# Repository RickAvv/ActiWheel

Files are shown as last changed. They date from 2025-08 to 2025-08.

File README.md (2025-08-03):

# ActiWheel
Complex activity wheel for mice behavioural research

The wheel is very simple in its implementation, as it has an arduino MEGA 2560 with a [logger shield](https://www.az-delivery.uk/products/datenlogger-modul) at its core.  The wheel axel is the shaft of a continuous potentiometer so that the exact position of the wheel in the radial axis can be logged, at a frequency of 100 Hz. 

The potentiometer it was designed to work with can be found [here](https://uk.rs-online.com/web/p/potentiometers/6930746), although any continuous potentiometer would do. A possible improvement on the design would come from the implementation of a rotary encoder instead of a potentiometer.  
  
## Assembly instructions:  
1) Print all the parts - the rungs have a bigger circular base for printing stability that should be snapped away with wire cutters or other tool.   
  
2) Assemble the Base and the Box with M3 countersunk screws of appropriate length.  

3) Attach the Arduino onto the Lid with M3 countersunk screws and M3 nuts. Mount the logger shield. Insert the SD card.  
  
4) Use dupont wires or soldering to connect the potentiometer to 5V, ground and A8 (middle potentiometer pin). Mount the potentiometer onto the Box with its hex nut. Slot the Connector onto the potentiometer shaft, and mount the Wheel onto the Connector with an M3 screw (center of Wheel).  
  
5) To power the arduino, externalise 2 wires from 5V and ground through the small slit on top of the Box, ideally soldered to a female 5V jack to be connected to a wall 9V power supply. Make sure to use plastic or metal shielding for the part that is still inside the mouse cage to avoid them being chewed.  
  
6) Mount the Lid onto the Box with countersank M3 screws.

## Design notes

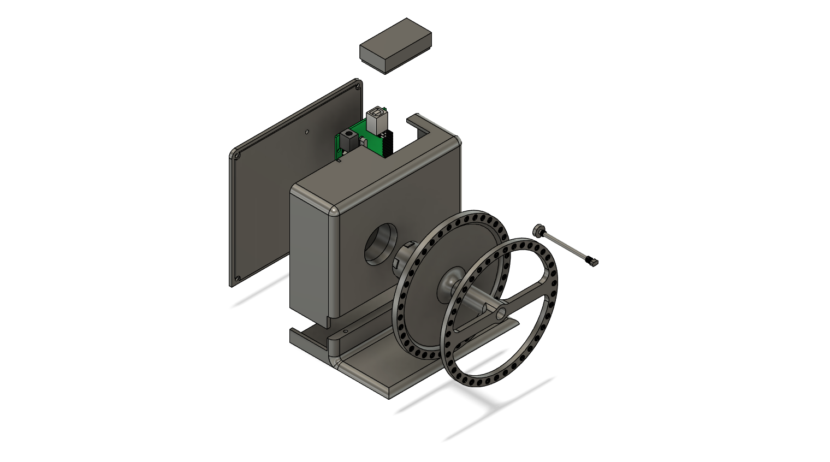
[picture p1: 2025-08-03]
stl_files/ActiWheel.png

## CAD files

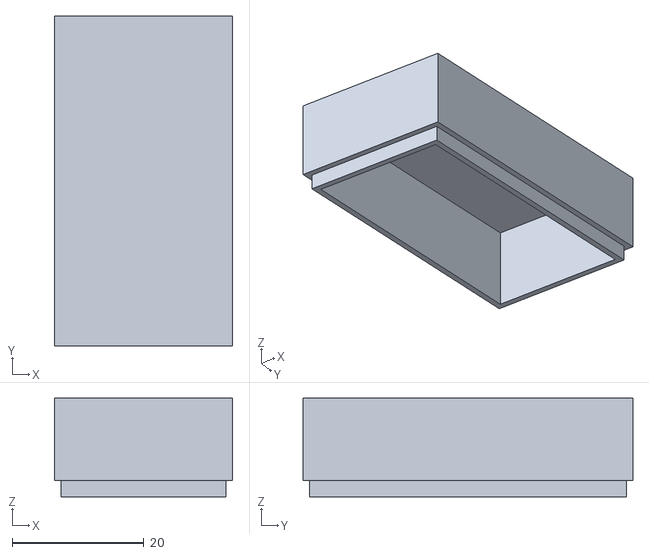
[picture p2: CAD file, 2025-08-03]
stl_files/Cap.stl
27.0 x 50.0 x 15.0

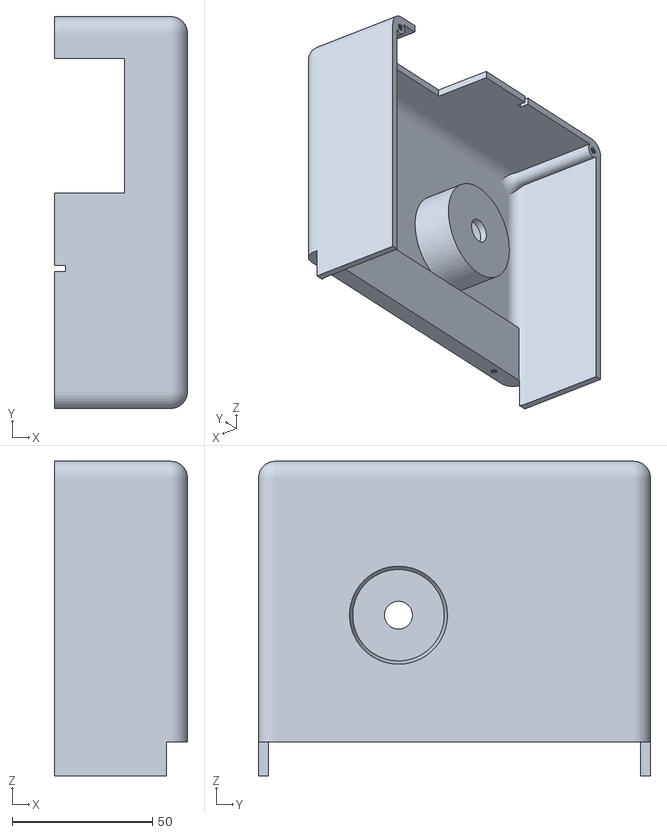
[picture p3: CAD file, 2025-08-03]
stl_files/Box.stl
47.5 x 140.0 x 112.4

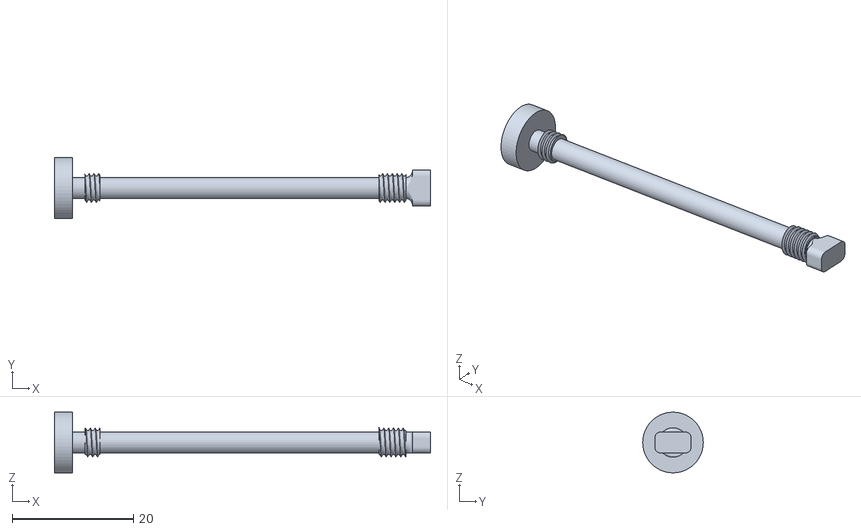
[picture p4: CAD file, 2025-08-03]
stl_files/Rung.stl
62.0 x 10.0 x 9.98

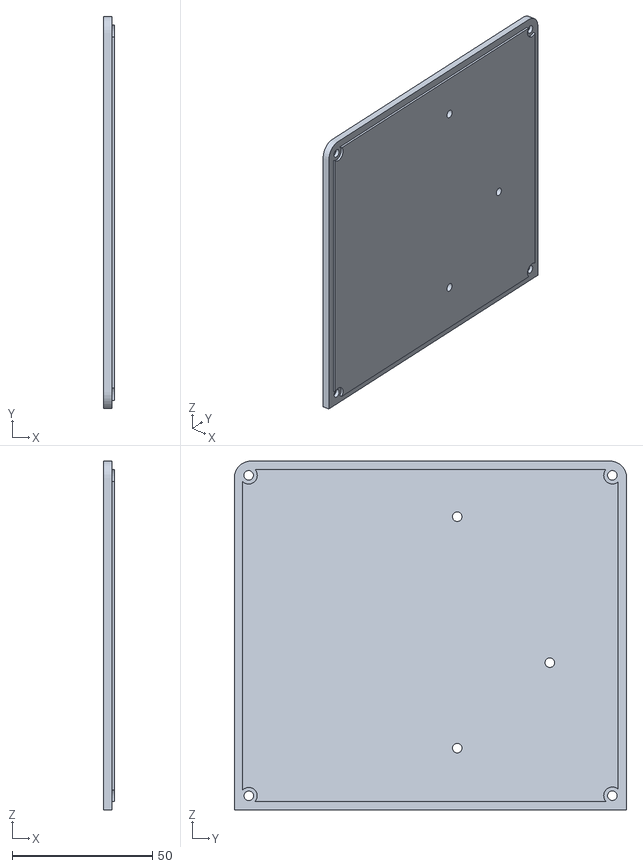
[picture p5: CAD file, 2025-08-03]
stl_files/Lid.stl
4.00 x 140.0 x 124.5

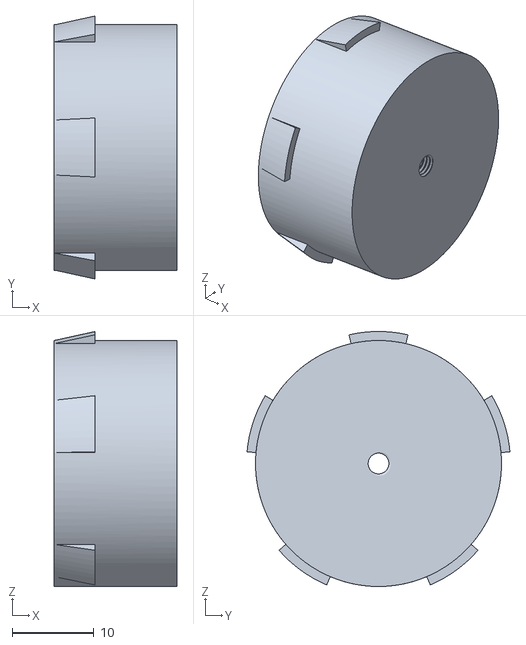
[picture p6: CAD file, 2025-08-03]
stl_files/Connector.stl
15.0 x 32.1 x 31.1

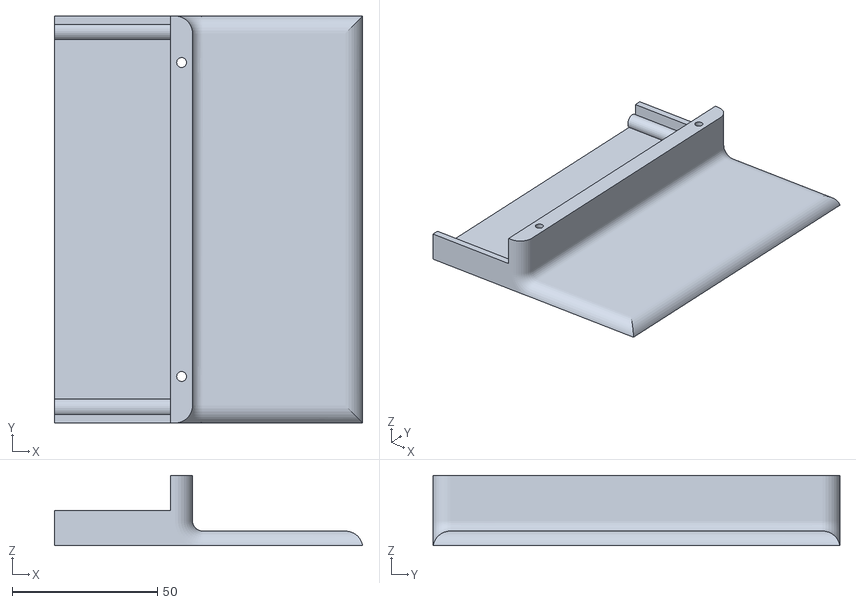
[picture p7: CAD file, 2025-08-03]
stl_files/Base.stl
106.0 x 140.0 x 24.1

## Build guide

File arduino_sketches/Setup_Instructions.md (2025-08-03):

# Instructions for Synchronizing Clocks on the Complex Wheels

0) Library Installation  
Download the following libraries (**Sketch -> Include Library -> Manage Libraries**) (only needed the first time):

    - `TimerThree`
    - `RTClib` (by Adafruit)
    - `SDfat` (by Bill Greiman – **NOT** the Adafruit fork)

1) Connect the Arduino via USB cable  
2) Open both sketches: `Sync_clock` and `ActiWheel`  
3) Select `Sync_clock` and open the Serial Monitor (magnifying glass icon in the top right)  
4) Click **Upload**  
5) Once upload is complete, you should see the current date and time printed in the Serial Monitor  
6) **Without closing or reopening the Serial Monitor**, select the `ActiWheel` sketch  
7) Modify line 57:

```cpp
sprintf(filename, "Wheel1_%04d-%02d-%02d_%02d-%02d-%02d.dat", now.year(), now.month(), now.day(), now.hour(), now.minute(), now.second());
```

Change the number in `Wheel1` according to the wheel you are using. This ensures that the filename includes the wheel number and avoids confusion when analyzing data from different wheels.

8) Click **Upload**  
9) The wheel is now ready

---

#### Note

The `Sync_clock` sketch forces the wheel’s internal clock to synchronize with the computer’s current time at the moment of compilation and upload. Every time the Arduino restarts, the clock is reset to that exact time.
For example:  
If you upload the sketch at 16:00, the clock will read 16:00.  
If you restart the Arduino at 16:10, after reboot the clock will again read 16:00.  
Therefore, it is important to upload the next sketch **without restarting the Arduino**, **disconnecting it**, or **closing/reopening the Serial Monitor**.

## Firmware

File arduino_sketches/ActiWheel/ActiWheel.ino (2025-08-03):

#include <TimerOne.h>
#include <TimerThree.h>
#include "RTClib.h"
#include <Wire.h>
#include <SPI.h>
#include <SdFat.h>   //user SDA/SCL on Pins 20 and 21

// file system
#if USE_SDIO
// Traditional DMA version.
// SdFatSdio sd;
// Faster version.
SdFatSdioEX sd;
#else  // USE_SDIO
SdFat sd;
#endif  // USE_SDIO

//SdFat sd;

SdFile logfile;
SdFile logfile2;
RTC_DS1307 RTC;

//Pins declaration
const uint16_t potPin = A8;
const uint16_t ledPin = 42;

uint32_t timestamp_main;

char filename[31];

const uint16_t bufferSize = 1020;

//volatile variables handled in the ISR
volatile uint8_t bufferA[bufferSize];
volatile uint8_t bufferB[bufferSize];
volatile uint16_t potRead_int;
volatile boolean mainWriteFlag = false;
volatile boolean useBufferA = true;
volatile uint16_t blockIndex = 0;
volatile uint32_t oldTimestamp = 0;
volatile uint32_t timestamp;
volatile uint32_t microsTime;

const uint32_t samplingFreq = 100;
volatile uint16_t sampleCounter = 0;

uint8_t nowHour;
uint8_t nowMinute;
uint8_t nowSecond;
uint8_t newfileHour = 0;
uint8_t newfileMinute = 0;
boolean newfileFlag = true;

void createLogfile() {
  DateTime now = RTC.now();
  sprintf(filename, "Wheel1_%04d-%02d-%02d_%02d-%02d-%02d.dat", now.year(), now.month(), now.day(), now.hour(), now.minute(), now.second());
  logfile.open(filename, O_WRITE | O_CREAT);
  Serial.println(filename);
}


void logData() {
  if (timestamp != oldTimestamp) {  //this is to avoid missed timestamp updates during occasional long latency writes
    oldTimestamp = timestamp;
    sampleCounter = 0;
  }
  sampleCounter++;
  if (sampleCounter > samplingFreq) { //it forces the timestamp to be incremented if 100 data points with that timestamp have already been acquired
    timestamp++;
    sampleCounter = 0;
  }
  potRead_int = analogRead(potPin);
  microsTime = micros();

  if (useBufferA) {                                             //The 2 buffers are used one at the time to avoid missing data.
    bufferA[blockIndex + 1] = uint8_t(potRead_int >> 8);        //As one gets full, it is written to the sd card during the loop()
    bufferA[blockIndex] = uint8_t(potRead_int);                 //so that the other buffer can be filled as the first one is written.
    bufferA[blockIndex + 5] = uint8_t(timestamp >> 24);
    bufferA[blockIndex + 4] = uint8_t(timestamp >> 16);
    bufferA[blockIndex + 3] = uint8_t(timestamp >> 8);
    bufferA[blockIndex + 2] = uint8_t(timestamp);
    bufferA[blockIndex + 9] = uint8_t(microsTime >> 24);
    bufferA[blockIndex + 8] = uint8_t(microsTime >> 16);
    bufferA[blockIndex + 7] = uint8_t(microsTime >> 8);
    bufferA[blockIndex + 6] = uint8_t(microsTime);

    blockIndex = blockIndex + 10;
  }
  else {
    bufferB[blockIndex + 1] = uint8_t(potRead_int >> 8);
    bufferB[blockIndex] = uint8_t(potRead_int);
    bufferB[blockIndex + 5] = uint8_t(timestamp >> 24);
    bufferB[blockIndex + 4] = uint8_t(timestamp >> 16);
    bufferB[blockIndex + 3] = uint8_t(timestamp >> 8);
    bufferB[blockIndex + 2] = uint8_t(timestamp);
    bufferB[blockIndex + 9] = uint8_t(microsTime >> 24);
    bufferB[blockIndex + 8] = uint8_t(microsTime >> 16);
    bufferB[blockIndex + 7] = uint8_t(microsTime >> 8);
    bufferB[blockIndex + 6] = uint8_t(microsTime);

    blockIndex = blockIndex + 10;
  }

  if (blockIndex >= bufferSize) {
    useBufferA = !useBufferA;
    blockIndex = 0;
    mainWriteFlag = true;
  }
}


void error() {
  while (true) {
    digitalWrite(ledPin, HIGH);
    delay(500);
    digitalWrite(ledPin, LOW);
    delay(500);
  }
}


void setup() {
  Serial.begin(115200);
  Wire.begin();
  RTC.begin();
  SPI.begin();

  pinMode(potPin, INPUT);
  pinMode(ledPin, OUTPUT);
  digitalWrite(ledPin, HIGH);
  delay(1000);

  if (!sd.begin(53)) {
    Serial.println("card not present");
    error();
  }
  else {
    Serial.println("card initialized");
    digitalWrite(ledPin, LOW);
  }

  createLogfile();

  if (sd.exists(filename)) {
    Serial.println("Logging...");
  }
  else {
    Serial.println("Could not create log file");
    error();
  }
  uint32_t samplingInterval = 1000000 / samplingFreq;
  
  Timer3.initialize();
  Timer3.setPeriod(samplingInterval);
  Timer3.attachInterrupt(logData);
}


void loop() {
  DateTime now = RTC.now();
  timestamp_main = now.unixtime();

  nowHour = now.hour();
  nowMinute = now.minute();
  nowSecond = now.second();

  noInterrupts();
  timestamp = timestamp_main;
  interrupts();

  if (mainWriteFlag) {
    if (useBufferA) {
      logfile.write((uint8_t *)&bufferB, sizeof(bufferB));
      logfile.sync();
      mainWriteFlag = false;
    }
    else {
      logfile.write((uint8_t *)&bufferA, sizeof(bufferA));
      logfile.sync();
      mainWriteFlag = false;
    }
  }
}

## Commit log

2025-08-03 arduino sketches to setup clock and for the core functioning of the wheel, with instructions
2025-08-03 STL files for 3D printing
    [Base.stl, Box.stl, Cap.stl, Connector.stl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]
2025-08-03 Added assembly instructions and product links
